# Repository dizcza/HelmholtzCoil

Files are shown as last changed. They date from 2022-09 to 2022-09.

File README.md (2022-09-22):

# Helmholtz coil simulation and 3D model

Forked from

http://hackaday.io/project/7409-highly-configurable-3d-printed-helmholtz-coil

## Summary

Helmholtz coils contain a region of uniform magnetic field which is common used to measure the strength of magnets, measure electrical charges at the atomic level and nulling out earths magnetic field. The magnetic field calculation is done for you.

## 3D model

[Helmholtz.scad](Helmholtz.scad)

This project uses OpenScad which is a 3D Solid modeler for 3D printing. OpenScad has the advantage that it's a programming language, which lends itself to heavy customization. You can custom everything, and if you don't like it or need something else, then change it.

The inner cylinder of the coils (the space that is 1/3 the diameter of coil), denotes the area of uniform magnetic field.

The platform for magnetic experiments is replaceable, so you can have switchable platforms for applications.

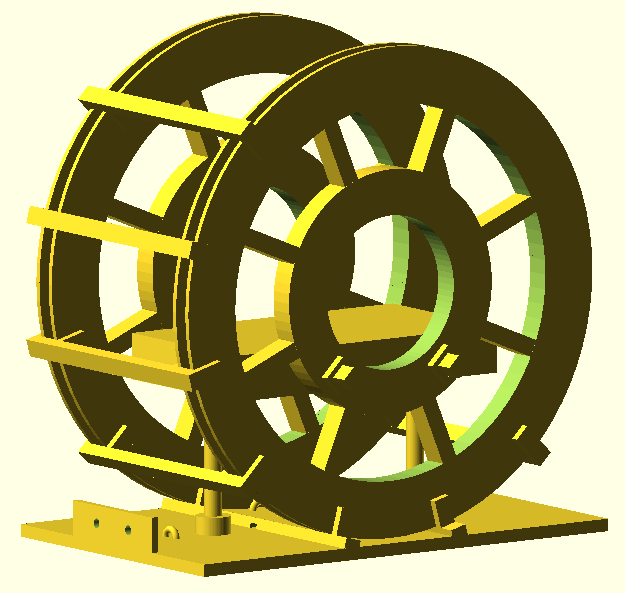
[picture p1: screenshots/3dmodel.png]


## Simulation

[helmholtz.py](helmholtz.py)

### Helmholtz Coil Configuration Statistics

    Mechanics
        Radius: 130 (inner 124.80) mm
        8 layers (H=10.40) of 6 wires (W=7.80)
        Packed winding (mm): H=9.22, W=8.45
        Winding enter & exit: same side
        Wire L=78.67 m, M=0.415 kg
             Litz 0.1 mm x 75 strands
        Physical diameter: 276.4 mm
    Circuit
        Resistance DC: 2.30 Ohm
        Resistance 1kHz: 16.31 Ohm
        Inductance: 2.57 mH
        Current: 2 A
    Magnetics
        B0 at center: 0.664 mT
        Homogeneous region (tol=0.01): 81 mm

### Quick launch

The simulation is executed in Python with Magpylib. To replicate the simulation, run

```
$ pip install -r requirements.txt
$ python helmholtz.py
```

### Magpylib simulation

The coil is simulated as a set of closed loop currents of the same direction (winding).
On the figure below, the coils are oriented vertically, and the uniform magnetic field in the center of the coils is oriented along the X axis.
The distance between the coil equals the coil radius (*Helmholtz coil*).

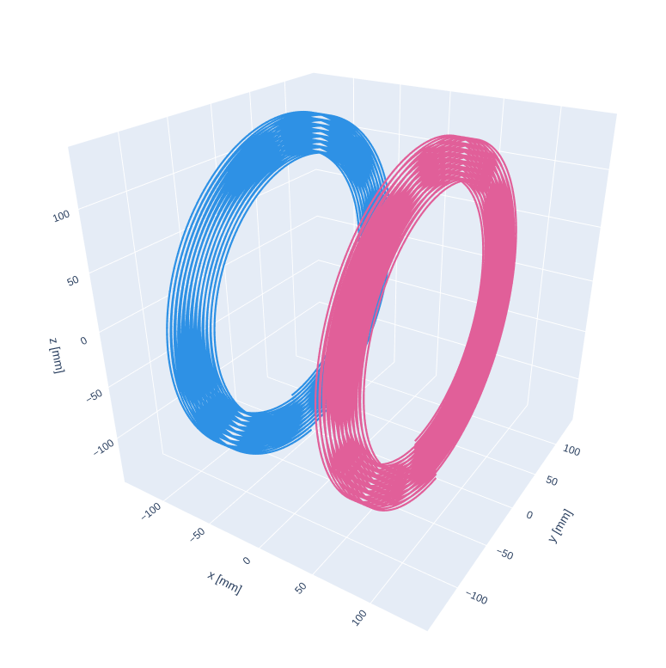
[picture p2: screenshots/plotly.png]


Magnetic field and its strength along the X axis is shown below.

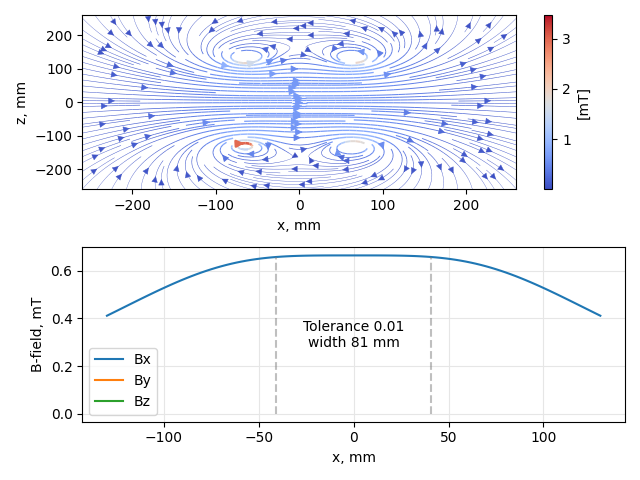
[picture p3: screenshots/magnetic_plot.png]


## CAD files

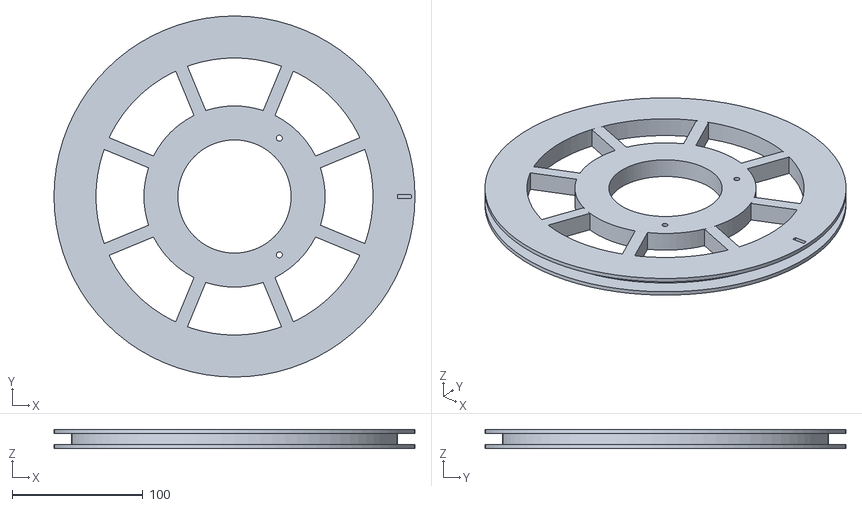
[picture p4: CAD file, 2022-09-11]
stl/part3_CoilFull.stl
276.4 x 276.4 x 14.8

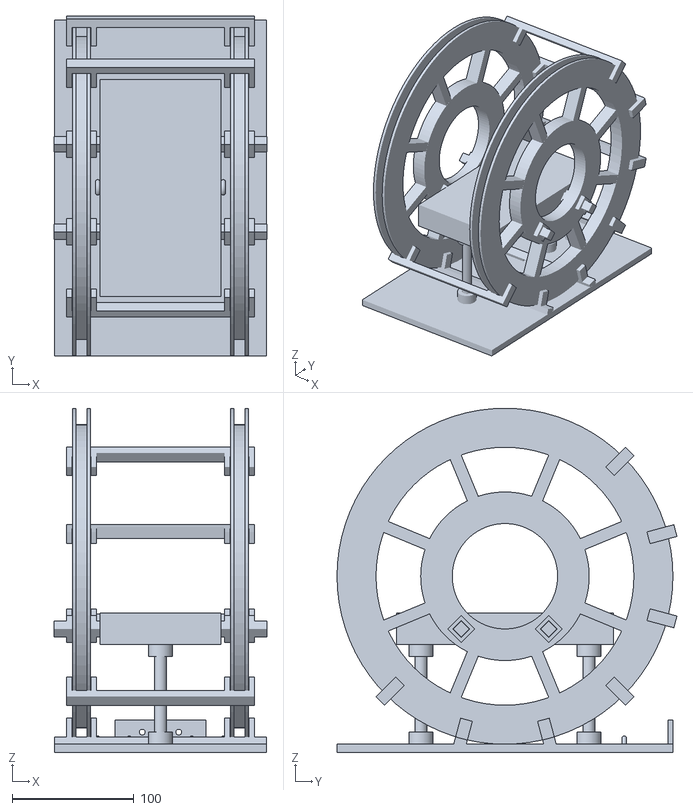
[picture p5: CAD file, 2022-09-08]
stl/part0_HelmholtzAssembled.stl
174.9 x 279.7 x 283.4

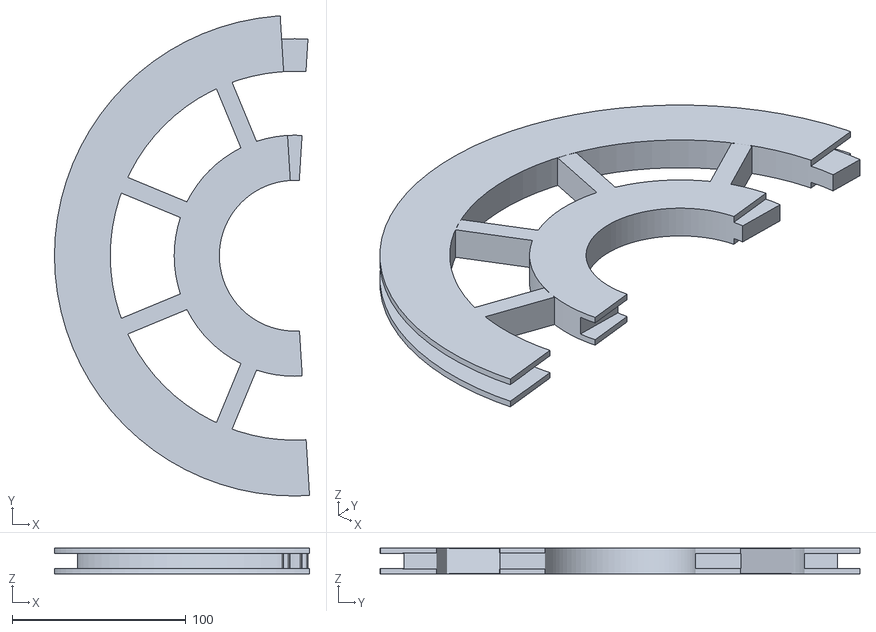
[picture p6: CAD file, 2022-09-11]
stl/part2_CoilHalf2.stl
146.7 x 276.1 x 14.8

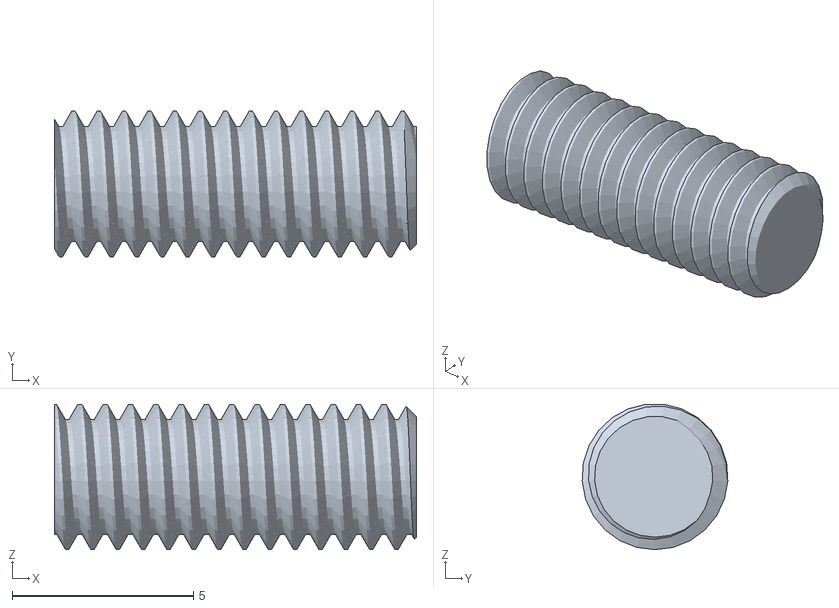
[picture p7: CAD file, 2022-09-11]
stl/part11_M4_thread_test.stl
10.0 x 4.03 x 4.02

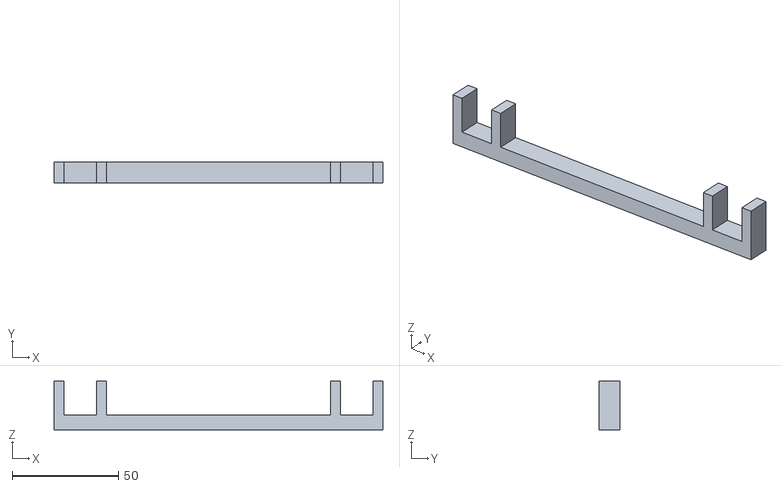
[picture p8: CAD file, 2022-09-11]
stl/part5_Retainers.stl
154.8 x 10.0 x 23.0

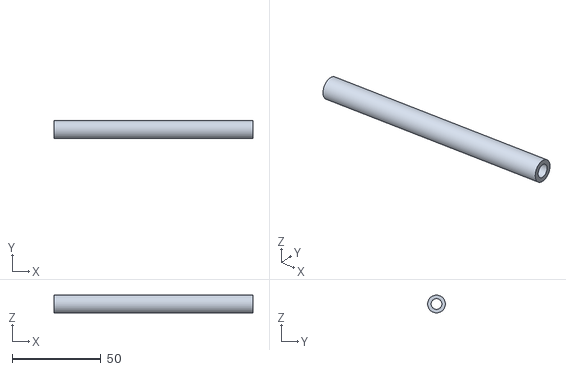
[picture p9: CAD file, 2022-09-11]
stl/part6_Pillars.stl
112.2 x 10.0 x 10.0

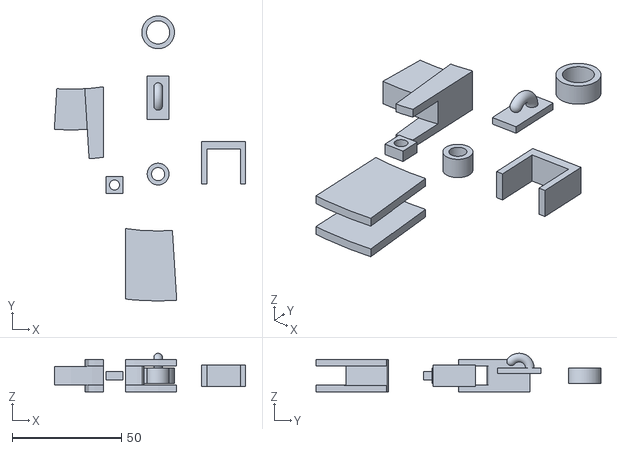
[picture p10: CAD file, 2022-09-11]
stl/part9_TestParts.stl
87.8 x 130.7 x 17.7

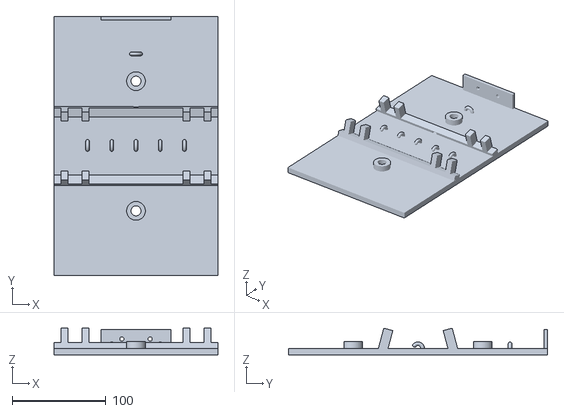
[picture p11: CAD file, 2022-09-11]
stl/part8_Platform.stl
174.8 x 276.4 x 28.4

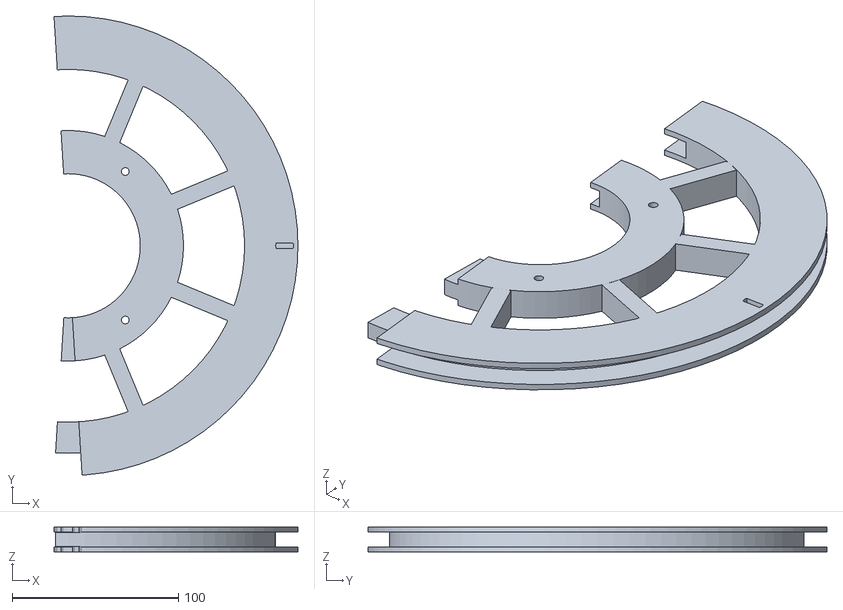
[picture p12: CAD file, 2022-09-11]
stl/part1_CoilHalf1.stl
146.7 x 276.1 x 14.8

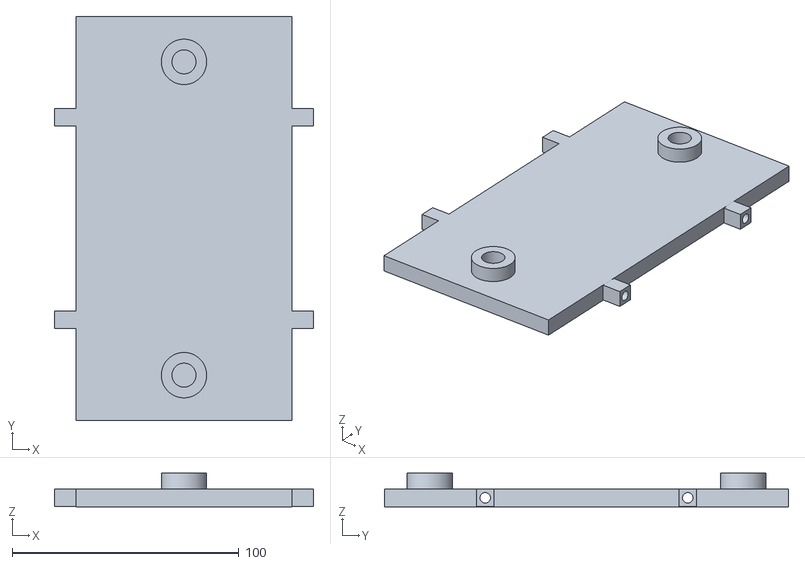
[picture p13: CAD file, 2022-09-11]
stl/part7_PlatformTable.stl
114.4 x 178.2 x 14.9

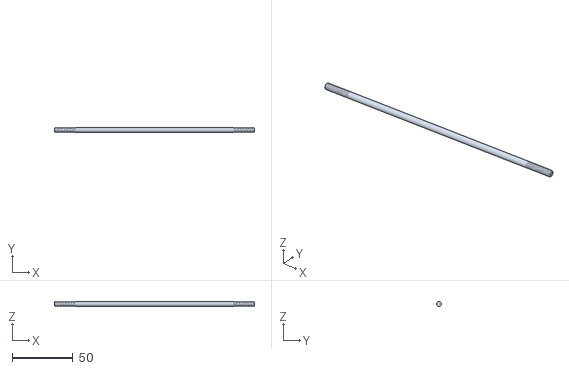
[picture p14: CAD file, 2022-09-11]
stl/part4_HorizontalBarsSupport.stl
164.8 x 4.03 x 4.03

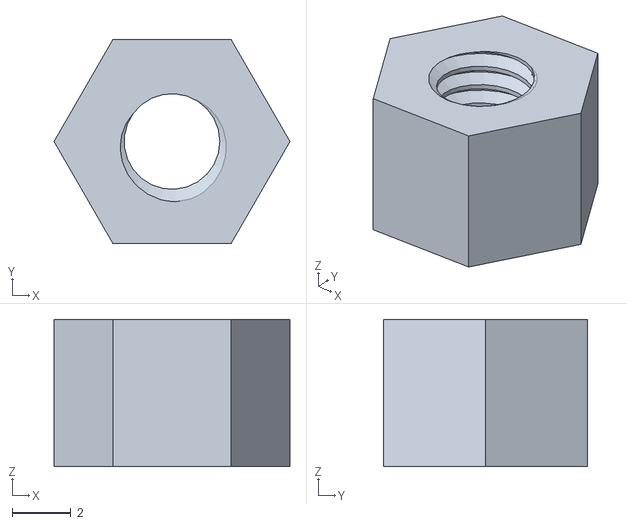
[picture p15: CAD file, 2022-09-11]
stl/part10_M4_nut.stl
8.00 x 6.93 x 5.00

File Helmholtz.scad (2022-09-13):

// Copyright: Jetty, 2015
// License: Creative Commons:  Attribution, Non-Commercial, Share-alike: CC BY-NC-SA
// https://creativecommons.org/licenses/by-nc-sa/2.0/

// Helmholtz Coil Design for 3D Printing.  Also this shows statistics about the coil generated, including the
// amount of field generated for a given number of wraps and current.

// Note: The coil diameter  + 2 * flange height must not exceed the width  of the 3D printer bed, and
// 		 The coil radius must not exceed the depth of the 3D printer bed.

// When winding the coils, both coils are wound in the same direction and mounted in the same direction, i.e. the current
// and magentic field in both coils is in the same axis.

// This will also do the calculation to figure out the magentic field strength
// Look in the output of openscad for "Helmholtz Coil Configuration Statistics" 
// Units are predominately nanoTesla (nT), as the earths field is generally measured in nT for magnetometers, if you need Gauss:
// 		1 Guass = 100,000nanoTesla

// Earths field is approximate +/-50,000nT, therefore the coil needs to be capable of at least that if cancelling the earths fields is required
// Kp Index 9 (highest for Aurora) is 500nT difference

// Printing:
//		If the diameter of the coil fits on the printer bed, then print 3 (CompleteCoil), otherwise if the radius of the coil
//		fits on the printed bed, then print 1 and 2 (the coil halves)
//
//		Coil halves - 10% infill, 2 shells and full support (including exterior)
//		table - 5% infill, 2 shells
//		Everything else, 10% infill, 2 shells
//
// Assembly:
//		Note the bottom of each coil has a small hole for the wire to go through, when assembling coil halves, make sure you have that
//		hole in each assembled coil.


use <threads.scad>

// All the following settings are metric except coilOhmsPerThousandFeet and control the magnetic strength, size of
// the coil and statistics for the coil, they need to be set correctly
coilRadius						= 130;		// Coil Radius in mm's
coilLayersNum                   = 8;
coilWiresNum                    = 6;

COIL_RADIUS_REFERENCE           = 130;
SCALE_FACTOR                    = coilRadius / COIL_RADIUS_REFERENCE;
SCALE_FACTOR_SQRT               = getScaleFactor();

wireDiamNominal                 = 1.2;
wireDiam				        = wireDiamNominal + 0.1;		// Wire diameter in mm's, note this includes insulation (insulation thickness varies)
windingFudge			        = 0.3;		// Fudge factor in mm's to add to the space for the coil to allow for 3D printer inaccuracy	
coilWindingWidth	            = wireDiam * coilWiresNum + windingFudge;	// The space for the wire to fit in on the former
coilWindingHeight               = wireDiam * coilLayersNum;
coilFlangeHeightPad             = 3.0;
coilFlangeWidth		        	= max(2.0, 3.0 * SCALE_FACTOR_SQRT);

// Bottom winding begins
coilWindingRadiusInner          = coilRadius - coilWindingHeight / 2;

// Physical size of the coil
coilFlangeRadius                = coilWindingRadiusInner + coilWindingHeight + coilFlangeHeightPad;

coilHomogeneousDiam				= coilRadius * 2/3;
coilTotalThickness		= coilWindingWidth + coilFlangeWidth * 2;


coilOuterRingThickness = 0.15 * coilWindingRadiusInner;
coilInnerRingThickness = 0.3 * coilHomogeneousDiam;

coilOuterRingBottomRadius = coilWindingRadiusInner - coilOuterRingThickness;

coilHomogeneousRingCenterRadius = coilHomogeneousDiam / 2 + coilInnerRingThickness / 2;

coilFlangeOffset			= [0, 0, (coilWindingWidth + coilFlangeWidth) / 2];

// These settings effect parts of the total object
retainerCoilHolderThickness	= max(2.0, 5.0 * SCALE_FACTOR);
retainerCoilHolderThicknessBottom = 1.5 * retainerCoilHolderThickness;
retainerCoilHolderHeight    = (coilFlangeRadius - coilOuterRingBottomRadius) / 2;
retainerWidth				= max(4.0, 10.0 * SCALE_FACTOR);
retainerDepth				= max(2.0, 7.0 * SCALE_FACTOR_SQRT);

platformThickness		= 7.0 * SCALE_FACTOR_SQRT;
platformLength			= 2.0 * coilFlangeRadius;

wallUserThickness		= max(3.0, 4.0 * SCALE_FACTOR_SQRT);
wallUserHoleDiam		= 5.5;  // M4

tableThickness				= 8.0;
pillarDiam			        = 10 * SCALE_FACTOR_SQRT;

manifoldCorrection 				= .1;

cylinderFudge	= 0.4;
cylinderReinforcementDiameter	= pillarDiam + 10 * SCALE_FACTOR_SQRT; 
cylinderReinforcementHeight	= platformThickness;

retainerLength         = coilRadius + coilTotalThickness + 2 * retainerCoilHolderThickness;

platformPad            = 10 * SCALE_FACTOR_SQRT;
platformWidth         = retainerLength + 2 * platformPad;

retainerAngleStep           = 30;
retainerLocationAngles		= [-1.5 * retainerAngleStep, 1.5 * retainerAngleStep, 2.5 * retainerAngleStep, 3.5 * retainerAngleStep, 4.5 * retainerAngleStep];
retainerLocationAnglesBlock	= [-retainerAngleStep / 2, retainerAngleStep / 2];

platformCenterZ			= - (coilFlangeRadius + platformThickness / 2);


retainerCenterY = coilFlangeRadius * sin(0.5 * retainerAngleStep);
pillarOutsideCenterY = coilFlangeRadius * sin(retainerAngleStep);

TABLE_INSIDE = coilRadius >= 150;
pillarCenterX = getPillarCenterX();
pillarCenterY = TABLE_INSIDE ? retainerCenterY / 2 : pillarOutsideCenterY;
tableCenterZ			= -(tableThickness / 2 + coilHomogeneousDiam / 2) + 0.15 * coilHomogeneousDiam;

tableCoilPad            = max(2.0, 10.0 * SCALE_FACTOR_SQRT);
tableWidth              = coilRadius - coilTotalThickness - 2 * tableCoilPad;
tableHoleY              = sqrt(pow(coilHomogeneousRingCenterRadius, 2) - pow(tableCenterZ, 2));
tableHoleSize = tableThickness / 2;
horizBarHoleDiam = tableHoleSize + 2 * cylinderFudge;


threadPitch = 0.7;  // M4
nutHeight = 5.0;


HorizontalBarSupportLen = coilRadius + coilTotalThickness + 4 * nutHeight;

tablePillarPad = tableThickness / 2;

pillarHeight				= tableCenterZ - platformCenterZ + (platformThickness + tableThickness) / 2 - tablePillarPad;
pillarCenterZ 		= platformCenterZ + (pillarHeight - platformThickness) / 2;

$fn = 80;

function getScaleFactor() = coilRadius > COIL_RADIUS_REFERENCE ? pow(SCALE_FACTOR, 0.75) : SCALE_FACTOR;

function getPillarCenterX() = let (centerX = 0.5 * (coilRadius / 2 - coilTotalThickness / 2)) centerX > 1.5 * cylinderReinforcementDiameter ? centerX : 0;

function getPillarFlipSingsX() = pillarCenterX > 0 ? [-1, 1] : [1];


partnum = 6;

if (partnum == 0) {
    echo(">>> Physical coil diameter (same as platform length) ", 2 * coilFlangeRadius);
    echo(">>> Platform width ", platformWidth);

    translate([0, 0, platformCenterZ]) drawPlatform();
    translate([0, 0, tableCenterZ]) drawPlatformTable();
    drawRetainersOnScene();
    drawHelmholtzCoilsOnScene();
    drawHorizontalBarSupportOnScene();
    drawNutsOnScene();
    drawTablePillarsOnScene();
}

/* FLAT COILS */
if (partnum == 1) bottomHalfHelmholtzCoil();
if (partnum == 2) topHalfHelmholtzCoil();
if (partnum == 3) helmholtzSingleCoil();

/* FLAT REST OF THE MODELS */
if (partnum == 4) drawHorizontalBarSupport();  // 2 pcs
if (partnum == 5) drawRetainer();  // 4 pcs
if (partnum == 6) rotate([0, 90, 0]) drawPillar();  // 2 pcs
if (partnum == 7) rotate([180, 0, 0]) drawPlatformTable();
if (partnum == 8) drawPlatform();
if (partnum == 9) drawTestParts();
if (partnum == 10) M4_nut();  // 4 pcs
if (partnum == 11) rotate([0, 90, 0]) M4_thread(length=2*nutHeight);


module drawTestParts() {
   
    module testWireHook() {
        translate([0, 20, 0])
        intersection() {
            drawPlatform();
            
            translate( [0, 0, platformThickness] )
            cube( [10, 20, 12], center=true );
        }
    }
    
    module testPillar() {
        heightDraw = cylinderReinforcementHeight;
        
        translate([0, -15, 0])
        intersection() {
            translate([0, 0, -pillarHeight / 2 + heightDraw / 2])
            drawPillar();
            cube([pillarDiam, pillarDiam, heightDraw], center=true);
        }
    }
    
    module testCoilRetainer() {
        retainerHeightWithDepth = retainerDepth + retainerCoilHolderHeight;
        
        translate([30, 0, 0])
        intersection() {
            translate([coilRadius / 2, 0, retainerDepth / 2])
            drawRetainer();
            
            translate([0, 0, retainerHeightWithDepth / 2])
            cube([coilTotalThickness + 2 * retainerCoilHolderThickness, retainerWidth, retainerHeightWithDepth], center=true);
        }
    }
    
    module testCoilHalfer(bottom=true) {
        coilHalfterTestCutSize = [30, 50, 50];
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

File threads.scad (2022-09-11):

/*
 * ISO-standard metric threads, following this specification:
 *          http://en.wikipedia.org/wiki/ISO_metric_screw_thread
 *
 * Copyright 2022 Dan Kirshner - dan_kirshner@yahoo.com
 * This program is free software: you can redistribute it and/or modify
 * it under the terms of the GNU General Public License as published by
 * the Free Software Foundation, either version 3 of the License, or
 * (at your option) any later version.
 *
 * This program is distributed in the hope that it will be useful,
 * but WITHOUT ANY WARRANTY; without even the implied warranty of
 * MERCHANTABILITY or FITNESS FOR A PARTICULAR PURPOSE.  See the
 * GNU General Public License for more details.
 *
 * See <http://www.gnu.org/licenses/>.
 *
 * Version 2.7.  2022-02-27  Increase minimum thread segments.
 * Version 2.6.  2021-05-16  Contributed patches for leadin (thanks,
                             jeffery.spirko@tamucc.edu) and aligning thread
                             "facets" (triangulation) with base cylinder
                             (thanks, rambetter@protonmail.com).
 * Version 2.5.  2020-04-11  Leadin option works for internal threads.
 * Version 2.4.  2019-07-14  Add test option - do not render threads.
 * Version 2.3.  2017-08-31  Default for leadin: 0 (best for internal threads).
 * Version 2.2.  2017-01-01  Correction for angle; leadfac option.  (Thanks to
 *                           Andrew Allen <a2intl@gmail.com>.)
 * Version 2.1.  2016-12-04  Chamfer bottom end (low-z); leadin option.
 * Version 2.0.  2016-11-05  Backwards compatibility (earlier OpenSCAD) fixes.
 * Version 1.9.  2016-07-03  Option: tapered.
 * Version 1.8.  2016-01-08  Option: (non-standard) angle.
 * Version 1.7.  2015-11-28  Larger x-increment - for small-diameters.
 * Version 1.6.  2015-09-01  Options: square threads, rectangular threads.
 * Version 1.5.  2015-06-12  Options: thread_size, groove.
 * Version 1.4.  2014-10-17  Use "faces" instead of "triangles" for polyhedron
 * Version 1.3.  2013-12-01  Correct loop over turns -- don't have early cut-off
 * Version 1.2.  2012-09-09  Use discrete polyhedra rather than linear_extrude ()
 * Version 1.1.  2012-09-07  Corrected to right-hand threads!
 */

// Examples.
//
// Standard M8 x 1.
// metric_thread (diameter=8, pitch=1, length=4);

// Square thread.
// metric_thread (diameter=8, pitch=1, length=4, square=true);

// Non-standard: long pitch, same thread size.
//metric_thread (diameter=8, pitch=4, length=4, thread_size=1, groove=true);

// Non-standard: 20 mm diameter, long pitch, square "trough" width 3 mm,
// depth 1 mm.
//metric_thread (diameter=20, pitch=8, length=16, square=true, thread_size=6,
//               groove=true, rectangle=0.333);

// English: 1/4 x 20.
//english_thread (diameter=1/4, threads_per_inch=20, length=1);

// Tapered.  Example -- pipe size 3/4" -- per:
// http://www.engineeringtoolbox.com/npt-national-pipe-taper-threads-d_750.html
// english_thread (diameter=1.05, threads_per_inch=14, length=3/4, taper=1/16);

// Thread for mounting on Rohloff hub.
//difference () {
//   cylinder (r=20, h=10, $fn=100);
//
//   metric_thread (diameter=34, pitch=1, length=10, internal=true, n_starts=6);
//}


// ----------------------------------------------------------------------------
function segments (diameter) = min (150, max (ceil (diameter*6), 25));


// ----------------------------------------------------------------------------
// diameter -    outside diameter of threads in mm. Default: 8.
// pitch    -    thread axial "travel" per turn in mm.  Default: 1.
// length   -    overall axial length of thread in mm.  Default: 1.
// internal -    true = clearances for internal thread (e.g., a nut).
//               false = clearances for external thread (e.g., a bolt).
//               (Internal threads should be "cut out" from a solid using
//               difference ()).  Default: false.
// n_starts -    Number of thread starts (e.g., DNA, a "double helix," has
//               n_starts=2).  See wikipedia Screw_thread.  Default: 1.
// thread_size - (non-standard) axial width of a single thread "V" - independent
//               of pitch.  Default: same as pitch.
// groove      - (non-standard) true = subtract inverted "V" from cylinder
//                (rather thanadd protruding "V" to cylinder).  Default: false.
// square      - true = square threads (per
//               https://en.wikipedia.org/wiki/Square_thread_form).  Default:
//               false.
// rectangle   - (non-standard) "Rectangular" thread - ratio depth/(axial) width
//               Default: 0 (standard "v" thread).
// angle       - (non-standard) angle (deg) of thread side from perpendicular to
//               axis (default = standard = 30 degrees).
// taper       - diameter change per length (National Pipe Thread/ANSI B1.20.1
//               is 1" diameter per 16" length). Taper decreases from 'diameter'
//               as z increases.  Default: 0 (no taper).
// leadin      - 0 (default): no chamfer; 1: chamfer (45 degree) at max-z end;
//               2: chamfer at both ends, 3: chamfer at z=0 end.
// leadfac     - scale of leadin chamfer length (default: 1.0 = 1/2 thread).
// test        - true = do not render threads (just draw "blank" cylinder).
//               Default: false (draw threads).
module metric_thread (diameter=8, pitch=1, length=1, internal=false, n_starts=1,
                      thread_size=-1, groove=false, square=false, rectangle=0,
                      angle=30, taper=0, leadin=0, leadfac=1.0, test=false)
{
   // thread_size: size of thread "V" different than travel per turn (pitch).
   // Default: same as pitch.
   local_thread_size = thread_size == -1 ? pitch : thread_size;
   local_rectangle = rectangle ? rectangle : 1;

   n_segments = segments (diameter);
   h = (test && ! internal) ? 0 : (square || rectangle) ? local_thread_size*local_rectangle/2 : local_thread_size / (2 * tan(angle));

   h_fac1 = (square || rectangle) ? 0.90 : 0.625;

   // External thread includes additional relief.
   h_fac2 = (square || rectangle) ? 0.95 : 5.3/8;

   tapered_diameter = diameter - length*taper;

   difference () {
      union () {
         if (! groove) {
            if (! test) {
               metric_thread_turns (diameter, pitch, length, internal, n_starts,
                                    local_thread_size, groove, square, rectangle, angle,
                                    taper);
            }
         }

         difference () {

            // Solid center, including Dmin truncation.
            if (groove) {
               cylinder (r1=diameter/2, r2=tapered_diameter/2,
                         h=length, $fn=n_segments);
            } else if (internal) {
               cylinder (r1=diameter/2 - h*h_fac1, r2=tapered_diameter/2 - h*h_fac1,
                         h=length, $fn=n_segments);
            } else {

               // External thread.
               cylinder (r1=diameter/2 - h*h_fac2, r2=tapered_diameter/2 - h*h_fac2,
                         h=length, $fn=n_segments);
            }

            if (groove) {
               if (! test) {
                  metric_thread_turns (diameter, pitch, length, internal, n_starts,
                                       local_thread_size, groove, square, rectangle,
                                       angle, taper);
               }
            }
         }

         // Internal thread lead-in: take away from external solid.
         if (internal) {

            // "Negative chamfer" z=0 end if leadin is 2 or 3.
            if (leadin == 2 || leadin == 3) {

               // Fixes by jeffery.spirko@tamucc.edu.
               cylinder (r1=diameter/2 - h + h*h_fac1*leadfac,
                         r2=diameter/2 - h,
                         h=h*h_fac1*leadfac, $fn=n_segments);
               /*
               cylinder (r1=diameter/2,
                         r2=diameter/2 - h*h_fac1*leadfac,
                         h=h*h_fac1*leadfac, $fn=n_segments);
               */
            }

            // "Negative chamfer" z-max end if leadin is 1 or 2.
            if (leadin == 1 || leadin == 2) {
               translate ([0, 0, length + 0.05 - h*h_fac1*leadfac]) {

                  cylinder (r1=tapered_diameter/2 - h,
                            h=h*h_fac1*leadfac,
                            r2=tapered_diameter/2 - h + h*h_fac1*leadfac,
                            $fn=n_segments);
                  /*
                  cylinder (r1=tapered_diameter/2 - h*h_fac1*leadfac,
                            h=h*h_fac1*leadfac,
                            r2=tapered_diameter/2,
                            $fn=n_segments);
                  */
               }
            }
         }
      }

      if (! internal) {

         // Chamfer z=0 end if leadin is 2 or 3.
         if (leadin == 2 || leadin == 3) {
            difference () {
               cylinder (r=diameter/2 + 1, h=h*h_fac1*leadfac, $fn=n_segments);
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

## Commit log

2022-09-03 added wire hole
    [Helmholtz.scad]
2022-09-04 wire box1
    [Helmholtz.scad]
2022-09-04 wire hooks
    [Helmholtz.scad]
2022-09-04 correcred coil radius for winding height
    [Helmholtz.scad]
2022-09-04 retainers holder height
    [Helmholtz.scad]
2022-09-04 fixed bug in coil wireHole()
    [Helmholtz.scad]
2022-09-04 added table support
    [Helmholtz.scad]
2022-09-04 naming convention
    [Helmholtz.scad]
2022-09-04 added halfers
    [Helmholtz.scad]
2022-09-05 scale factor
    [Helmholtz.scad]
2022-09-05 Pillars flat draw
    [Helmholtz.scad]
2022-09-05 2 or 4 pillars decided
    [Helmholtz.scad]
2022-09-05 draw test parts
    [Helmholtz.scad]
2022-09-05 added one more wire hook
    [Helmholtz.scad]
2022-09-05 fixed platform retainers depth in case radius is too large
    [Helmholtz.scad]
2022-09-05 added full 3d model
    [Helmholtz.scad, HelmholtzAssembled.stl]
2022-09-07 generate stl bash script
    [Helmholtz.scad]
2022-09-07 fixed bug in coil flanger width
    [Helmholtz.scad]
2022-09-07 reduced test figures
    [Helmholtz.scad]
2022-09-08 test banana plug hole part
    [Helmholtz.scad]
2022-09-08 upd stl files
    [CoilHalf1.stl, CoilHalf2.stl, CoilRetainers.stl, HelmholtzAssembled.stl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]
2022-09-09 don't draw reinforcement cube on coil
    [Helmholtz.scad]
2022-09-10 made bottom retainer thickness wider
    [Helmholtz.scad]
2022-09-11 threaded table support bar, M4 nut
    [Helmholtz.scad, threads.scad]
2022-09-11 drawPlatform at origin by default
    [Helmholtz.scad]
2022-09-11 removed drawRetainersFlat
    [Helmholtz.scad]
2022-09-12 rounded cylinder and cuts
    [Helmholtz.scad]
2022-09-12 fudge 0.2 mm for retainers
    [Helmholtz.scad]
2022-09-13 removed FUDGE_SIDE and made private fudges
    [Helmholtz.scad]
